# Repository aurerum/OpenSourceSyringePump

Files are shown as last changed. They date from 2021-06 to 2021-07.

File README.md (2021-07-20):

# Open Source Syringe Pump
Syringe pump designed for Empty Nose Syndrome

<h2>Introduction</H2>
I created this device to help people who suffer from Empty Nose Syndrome to sleep better.
This device has been designed to inject physiological serum in nose during night to moisten the nasal cavity and increase airflow sensation.

https://user-images.githubusercontent.com/80455782/126234150-841e0ce9-54df-4337-b9bd-3a2b1212d7b4.mp4

<h2>3D printed parts</h2>
The 3d files are in two folders for the both format .step and .stl, .stl can be used directly to print the part. .step is usefull if you want to modify the design.

<h2>Electronics parts</h2>
The project is based on the well know and cheap arduino nano micro controler which control a stepper motor via a motor driver.

<h2>Mechanical parts</h2>

<h2>Exploded views and nomenclature</h2>

Syringe pump exploded view
 
Syringe pump exploded view 2
     
Syringe pump exploded view 3

<table>
<tr>  
               <th colspan="4">Syringe pump</th>
</tr>                 
<tr>
               <th>Number</th>
               <th>Designation</th>
               <th>Quantity</th>
               <th>Where to buy ?</th>
              
</tr>
<tr>  
               <th colspan="4">3D printed parts</th>
</tr>
<tr>
               <td>1</td>
               <td>Main part n°1</td>
               <td>1</td>
               <td>-</td>
</tr>
<tr>
               <td>2</td>
               <td>Main part n°2</td>
               <td>1</td>
               <td>-</td>
 </tr>
 <tr>
               <td>3</td>
               <td>Carriage</td>
               <td>1</td>
               <td>-</td>
 </tr>
     
 <tr>
               <td>4</td>
               <td>Spacer</td>
               <td>4</td>
               <td>-</td>
 </tr>
 <tr>
               <td>5</td>
               <td>Stop ring</td>
               <td>2</td>
               <td>-</td>
 </tr>
 <tr>  
               <th colspan="4">Mechanical parts</th>
 </tr>
 <tr>
               <td>6</td>
               <td>T8 screw, length 150 mm + brass nut</td>
               <td>1</td>
               <td><a href="https://fr.aliexpress.com/item/32873975375.html?spm=a2g0s.9042311.0.0.27426c37Fw4uFA" target="_blank">T8 screw aliexpress</a></td>
 </tr>
 <tr>
               <td>7</td>
               <td>Shaft diameter 8 mm, lenght 130 mm</td>
               <td>2</td>
               <td><a href="https://fr.aliexpress.com/item/32890228043.html?spm=a2g0s.9042311.0.0.27426c37Fw4uFA" target="_blank">Shaft diameter 8 mm, lenght 130 mm aliexpress</a></td>
 </tr>
 <tr>
               <td>8</td>
               <td>Linear bearing diameter 8 mm, LMF8UU</td>
               <td>2</td>
               <td><a href="https://www.aliexpress.com/item/1005001469719209.html?spm=a2g0s.9042311.0.0.27426c37Fw4uFA" target="_blank">Linear bearing diameter 8 mm, LMF8UU aliexpress</a></td>
 </tr>
<tr>
               <td>9</td>
               <td>Coupleur 5 x 8</td>
               <td>1</td>
               <td><a href="https://www.aliexpress.com/item/32889118117.html?spm=a2g0s.9042311.0.0.27426c37Fw4uFA" target="_blank">Coupleur 5 x 8 aliexpress</a></td>
 </tr>
     
 <tr>
               <td>10</td>
               <td>Ball bearing, 608ZZ</td>
               <td>2</td>
               <td><a href="https://www.aliexpress.com/item/33016277396.html?spm=a2g0s.9042311.0.0.27426c37Fw4uFA" target="_blank">Ball bearing, 608ZZ aliexpress</a></td>
 </tr>
  <tr>  
               <th colspan="4">Electronic parts</th>
 </tr>
 <tr>
               <td>11</td>
               <td>Crash sensor</td>
               <td>2</td>
               <td><a href="https://www.dfrobot.com/product-762.html" target="_blank">Crash sensor DFRobot</a></td>
 </tr>
 <tr>
               <td>12</td>
               <td>Nema 17 stepper motor</td>
               <td>1</td>
               <td>You can buy this part in many places</td>
 </tr>

 <tr>  
               <th colspan="4">Screws</th>
 </tr>
 <tr>
               <td>13</td>
               <td>CHC M3 x 12</td>
               <td>4</td>
               <td>You can buy this in many places, be careful these are metric screws</td>
 </tr>
     
 <tr>
               <td>14</td>
               <td>CHC M3 x 6</td>
               <td>6</td>
               <td>You can buy this in many places, be careful these are metric screws</td>
 </tr>

 <tr>
               <td>15</td>
               <td>CHC M3 x 55</td>
               <td>4</td>
               <td>You can buy this in many places, be careful these are metric screws</td>
 </tr>
     
 <tr>
               <td>16</td>
               <td>CHC M3 x 20</td>
               <td>8</td>
               <td>You can buy this in many places, be careful these are metric screws</td>
 </tr>
     
 <tr>
               <td>17</td>
               <td>CHC M3 x 25</td>
               <td>4</td>
               <td>You can buy this in many places, be careful these are metric screws</td>
 </tr>
     
 <tr>
               <td>18</td>
               <td>M3 nut</td>
               <td>16</td>
               <td>You can buy this in many places, be careful these are metric screws</td>
 </tr>

</table>

exploded view electronic box
     
exploded view electronic box 2

<table>
<tr>  
               <th colspan="4">Electronic box</th>
</tr>                 
<tr>
               <th>Number</th>
               <th>Designation</th>
               <th>Quantity</th>
               <th>Where to buy ?</th>
              
</tr>
<tr>  
               <th colspan="4">3D printed parts</th>
</tr>
<tr>
               <td>1</td>
               <td>Box</td>
               <td>1</td>
               <td>-</td>
</tr>
<tr>
               <td>2</td>
               <td>Frame</td>
               <td>1</td>
               <td>-</td>
 </tr>

 <tr>  
               <th colspan="4">Electronic parts</th>
 </tr>
 <tr>
               <td>3</td>
               <td>Arduino nano</td>
               <td>1</td>
               <td><a href="https://www.dfrobot.com/product-786.html" target="_blank">Arduino nano DFRobot</a></td>
 </tr>
 <tr>
               <td>4</td>
               <td>Nano shield</td>
               <td>1</td>
               <td><a href="https://www.dfrobot.com/product-68.html" target="_blank">Nano shield DFRobot</a></td>
 </tr>
 <tr>
               <td>5</td>
               <td>Stepper driver, DRV8825 or TMC2208</td>
               <td>1</td>
               <td>You can buy this in many places</td>
 </tr>
 <tr>
               <td>6</td>
               <td>Stepper driver shield</td>
               <td>1</td>
               <td><a href="https://www.ebay.fr/itm/321589920004?hash=item4ae040c104:g:iOAAAOSwfyBbUHDG" target="_blank">Stepper driver shield ebay</a></td>
 </tr>
 <tr>
               <td>7</td>
               <td>Touch button</td>
               <td>3</td>
               <td><a href="https://fr.aliexpress.com/item/32570170116.html?spm=a2g0o.store_pc_groupList.8148356.5.34e0179ajqIRI4" target="_blank">Touch button aliexpress</a></td>
 </tr>
<tr>
               <td>8</td>
               <td>Jack adapter female 2.1 mm</td>
               <td>1</td>
               <td>You can buy this in many places</td>
 </tr>
 <tr>
               <td>-</td>
               <td>Female - female jumper wires </td>
               <td>1</td>
               <td><a href=https://www.dfrobot.com/product-356.html" target="_blank">Female - female jumper wires DFRobot</a></td>
 </tr>
                    
 <tr>  
               <th colspan="4">Screws</th>
 </tr>

 <tr>
               <td>9</td>
               <td>TBHC M3 x 8</td>
               <td>6</td>
               <td>You can buy this in many places, be careful these are metric screws</td>
 </tr>
                    
 <tr>
               <td>10</td>
               <td>CHC M3 x 6</td>
               <td>14</td>
               <td>You can buy this in many places, be careful these are metric screws</td>
 </tr>

 <tr>
               <td>11</td>
               <td>CHC M3 x 12</td>
               <td>4</td>
               <td>You can buy this in many places, be careful these are metric screws</td>
 </tr>
                    
 <tr>
               <td>12</td>
               <td>M3 nut</td>
               <td>6</td>
               <td>You can buy this in many places, be careful these are metric screws</td>
 </tr>
                    
 <tr>
               <td>13</td>
               <td>Spacer M3 x 10</td>
               <td>7</td>
               <td>You can buy this in many places, be careful these are metric screws</td>
 </tr>
</table>

<h2>Operation</h2>
Three touch buttons control the device, the two arrows are used to move forward and backward, it is the manual mode.
The disc on the center is the automatic mode, when it is pressed the carriage move forward a little bit each X minutes depending of what is programmed.

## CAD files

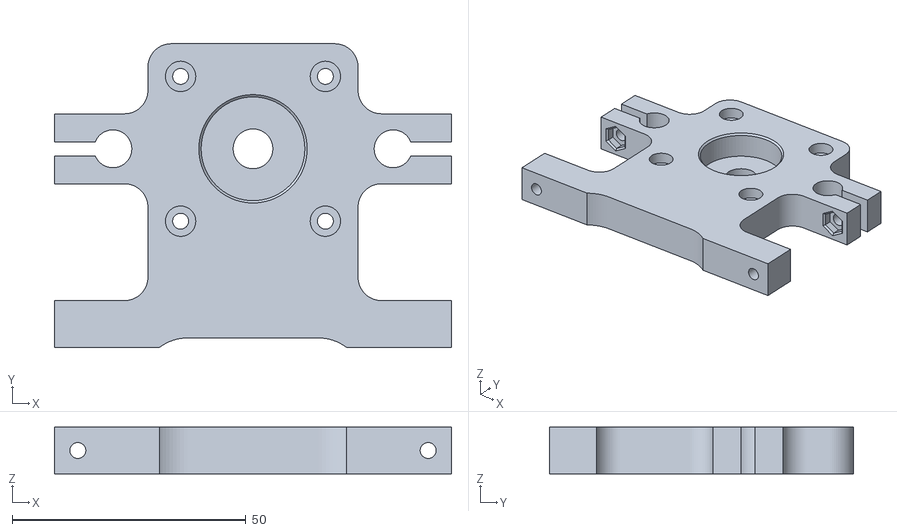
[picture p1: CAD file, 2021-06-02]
STL/Main part.STL
85.0 x 65.0 x 10.0

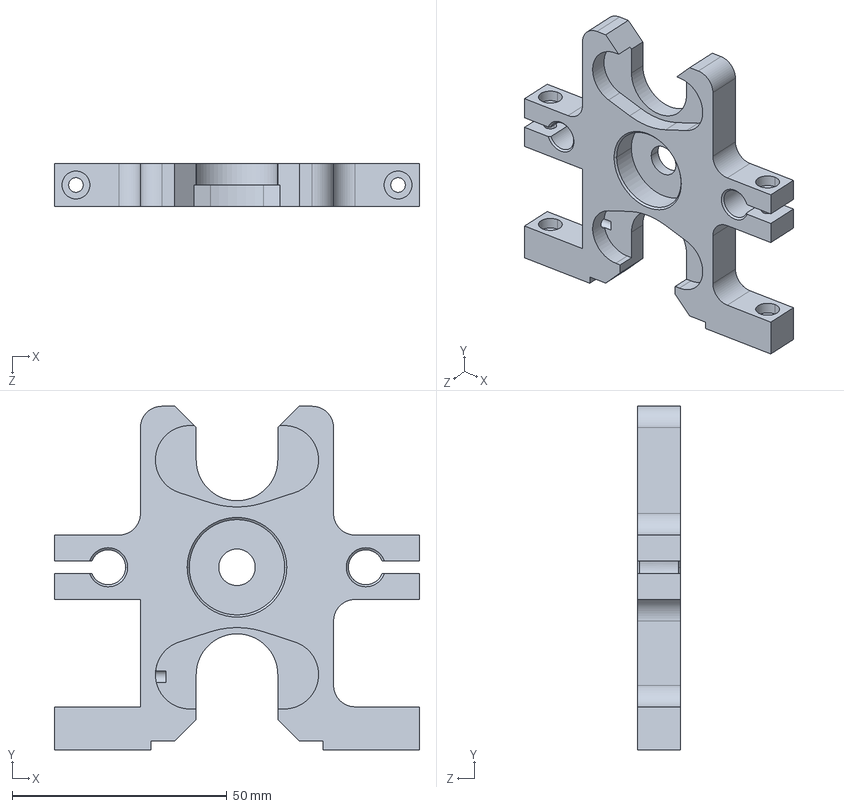
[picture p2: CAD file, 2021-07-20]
STEP/Main part n°2.STEP
85.0 x 80.0 x 10.0 mm

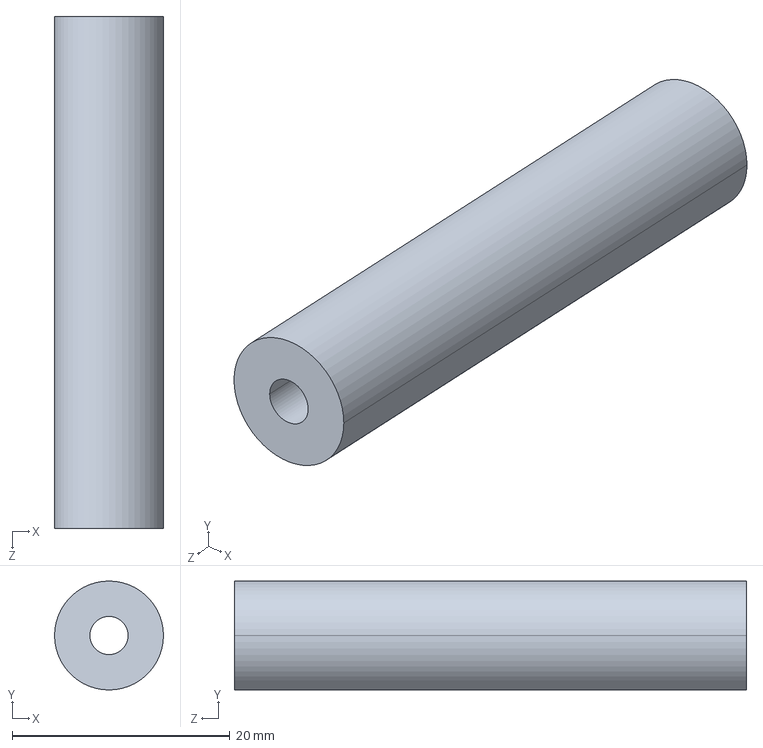
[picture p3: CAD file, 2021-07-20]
STEP/Spacer.STEP
10.0 x 10.0 x 47.0 mm

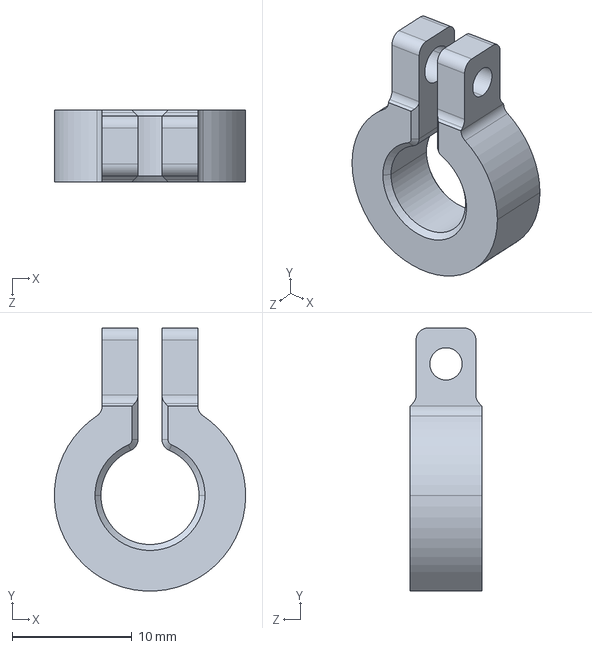
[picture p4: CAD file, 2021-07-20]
STEP/Stop ring.STEP
16.0 x 22.0 x 6.00 mm

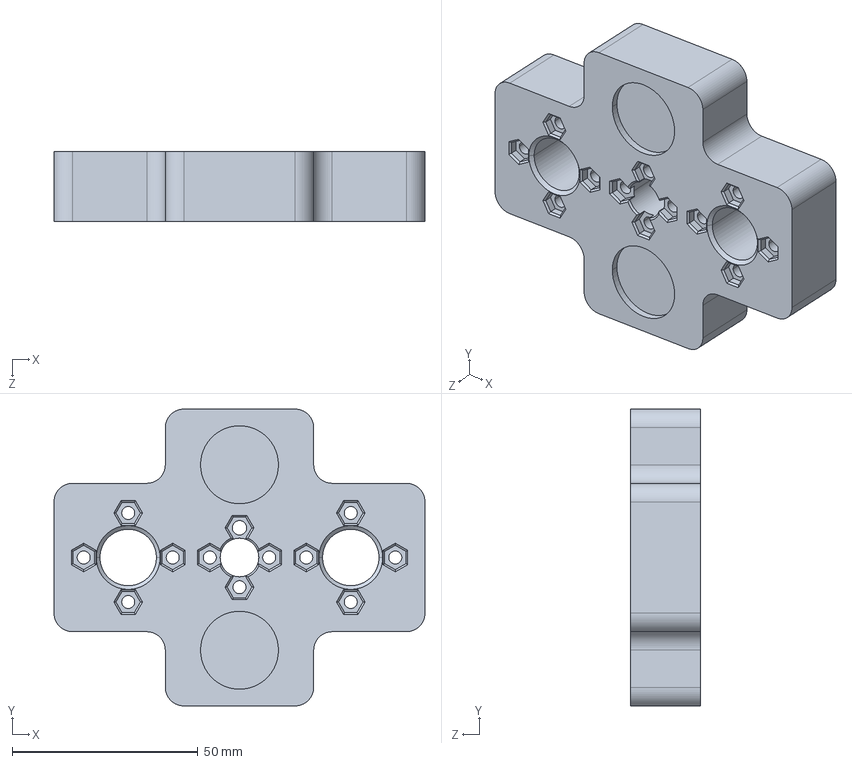
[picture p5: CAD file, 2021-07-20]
STEP/Carriage.STEP
100.0 x 80.0 x 19.0 mm

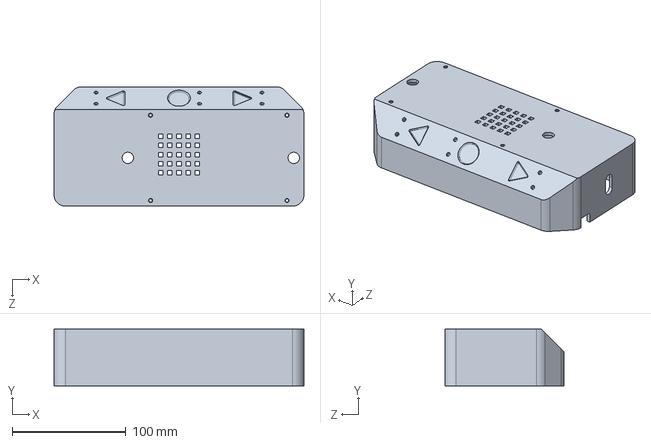
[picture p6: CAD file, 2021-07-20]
STEP/Electronic box.STEP
220.0 x 50.0 x 105.0 mm

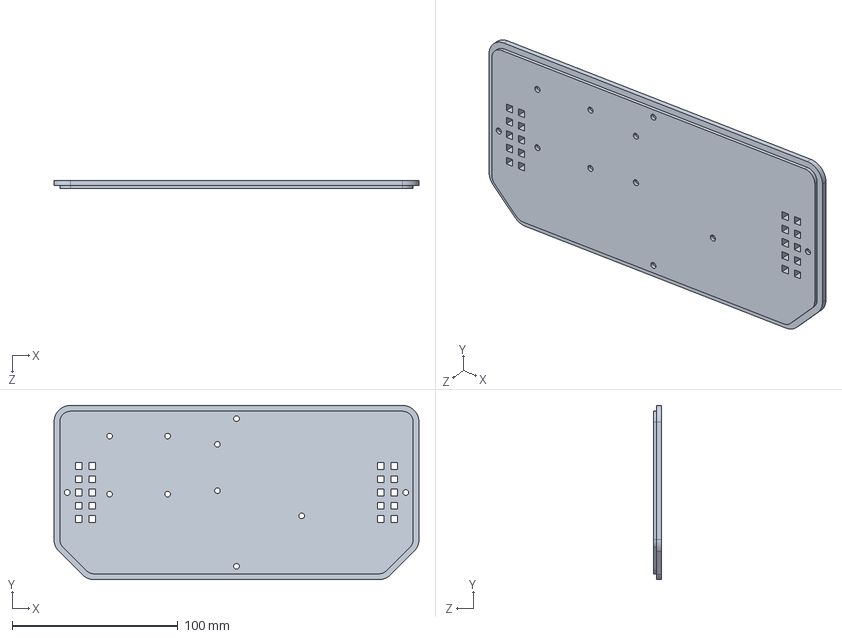
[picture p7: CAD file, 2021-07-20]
STEP/Electronic base.STEP
220.0 x 105.0 x 5.00 mm

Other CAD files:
STEP/Main part n°1.STEP
STL/Carriage.STL
STL/Electronic base.STL
STL/Electronic box.STL
STL/Main part n°2.STL
STL/Spacer.STL
STL/Stop ring.STL

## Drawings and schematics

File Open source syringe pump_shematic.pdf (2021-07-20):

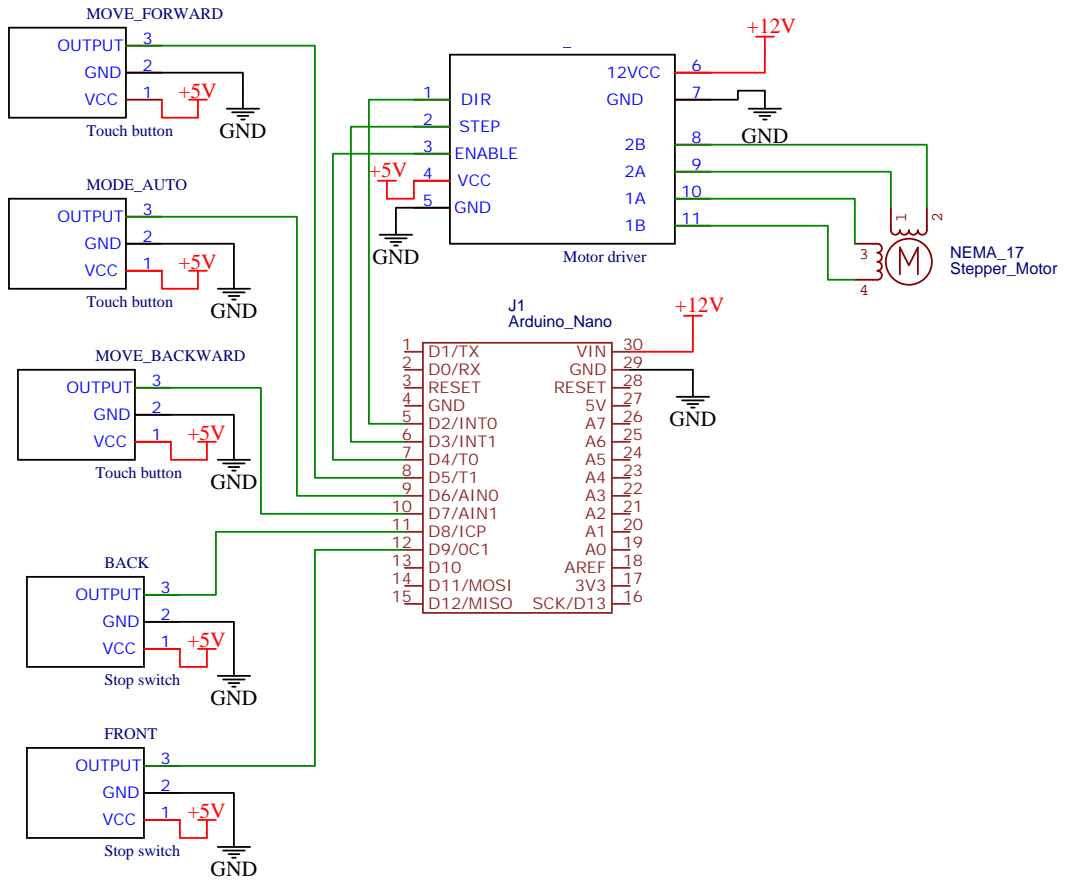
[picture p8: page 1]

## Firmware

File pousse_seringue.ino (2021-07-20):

// Include the AccelStepper library:
#include <AccelStepper.h>

// Define stepper motor an buttons connections and motor interface type. Motor interface type must be set to 1 when using a driver:
#define dirPin 2
#define stepPin 3
#define motorInterfaceType 1

const int enable = 4;
const int BPavance = 5;
const int BPrecule = 6;
const int BPauto = 7;
const int fd1 = 8;
const int fd2 = 9;

// /!\ Please only change these two values
//----------------------------------------------------------------------------
int timeCycle = 5; // Time between each injection in minutes
float distance = 0.16; //Distance traveled for each injection in millimeters
//----------------------------------------------------------------------------

int cycle = timeCycle * 600;
float stepQuantity = (distance * 3200)/8; 


bool fd1Val;
bool fd2Val;
bool BPavanceVal;
bool BPreculeVal;
bool BPautoVal;



// Create a new instance of the AccelStepper class:
AccelStepper stepper = AccelStepper(motorInterfaceType, stepPin, dirPin);

void setup() {
  // Set the maximum speed in steps per second:
  stepper.setMaxSpeed(1000);
  stepper.setAcceleration(10);


  pinMode(BPavance, INPUT);
  pinMode(BPrecule, INPUT);
  pinMode(BPauto, INPUT);
  pinMode(fd1, INPUT);
  pinMode(fd2, INPUT);
  pinMode(enable, OUTPUT);

  digitalWrite(enable, HIGH);

  Serial.begin(9600);

}

void loop() {

  
  Serial.println("arret");
  Serial.println(stepQuantity);
  Serial.println(cycle);
  digitalWrite(enable, HIGH);
  readInput();
  //Manual mode

  //Forward
  if (BPavanceVal == HIGH)
    {

      while(BPavanceVal == HIGH && fd2Val == HIGH)
      {
        digitalWrite(enable, LOW);
        stepper.setSpeed(1000);
        //dirPin sens avance
        stepper.runSpeed();
        readInput();
        Serial.println("Avance");
      }
  
      
    }

    

  //Backward
  if (BPreculeVal == HIGH)
    {
      
      
     while(BPreculeVal == HIGH && fd1Val == HIGH)
     {
        digitalWrite(enable, LOW);
        stepper.setSpeed(-1000);
        //dirPin sens recule
        stepper.runSpeed();
        readInput();
        Serial.println("Recule");
     }
      
    }

 //Auto mode
   if (BPautoVal == HIGH)
    {
       
      while (fd2Val == HIGH && BPreculeVal == LOW && BPavanceVal == LOW)
      {

        for (int i=0 ; i<=300 ; i++)
        {
          readInput();
          stepper.setCurrentPosition(0);
          while(stepper.currentPosition() != stepQuantity && fd2Val == HIGH && BPreculeVal == LOW && BPavanceVal == LOW )
            {
              digitalWrite(enable, LOW);
              stepper.setSpeed(40);
              stepper.runSpeed();
              Serial.println("auto");
              Serial.print("BP auto: ");
              Serial.println(BPautoVal);
              readInput();
            }

            digitalWrite(enable, HIGH);
            

            for (int j=0 ; j<=cycle ;j++)
            {
              readInput();
              if (fd2Val == LOW || BPreculeVal == HIGH || BPavanceVal == HIGH)
              {
                break;
                Serial.print("break");
              }
            delay(100);
            }
            
            
        }
        break;
        readInput();

      }
    }


  

}

void readInput(){

      fd1Val = digitalRead(fd1);
      fd2Val = digitalRead(fd2);
      BPavanceVal = digitalRead(BPavance);
      BPreculeVal = digitalRead(BPrecule);
      BPautoVal = digitalRead(BPauto);

}
